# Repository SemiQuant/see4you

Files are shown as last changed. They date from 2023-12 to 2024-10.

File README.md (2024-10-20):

# see4you

A portable OD600 spectrophotometer costing ~$30 (see BOM).
Has a similar dynamic range and comparable reading to the BioRad SmartSpec Plus.

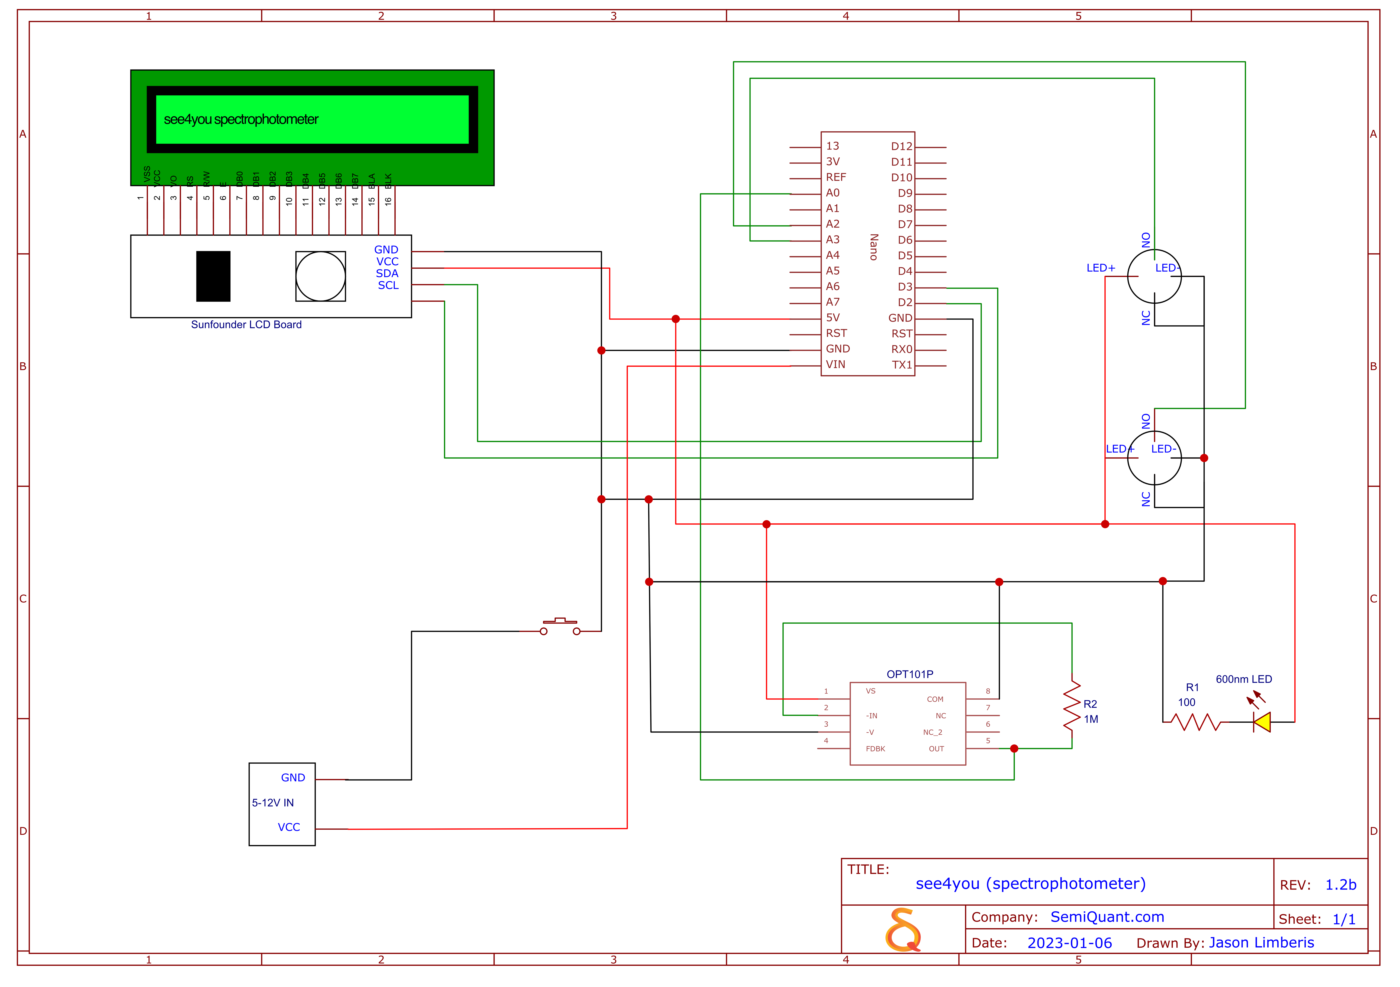
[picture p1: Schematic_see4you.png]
schematic


device

Usage video: 

https://github.com/SemiQuant/see4you/assets/8179171/b92d9823-f1b9-4fbb-b35a-ba92c5bc5852

## version 1b

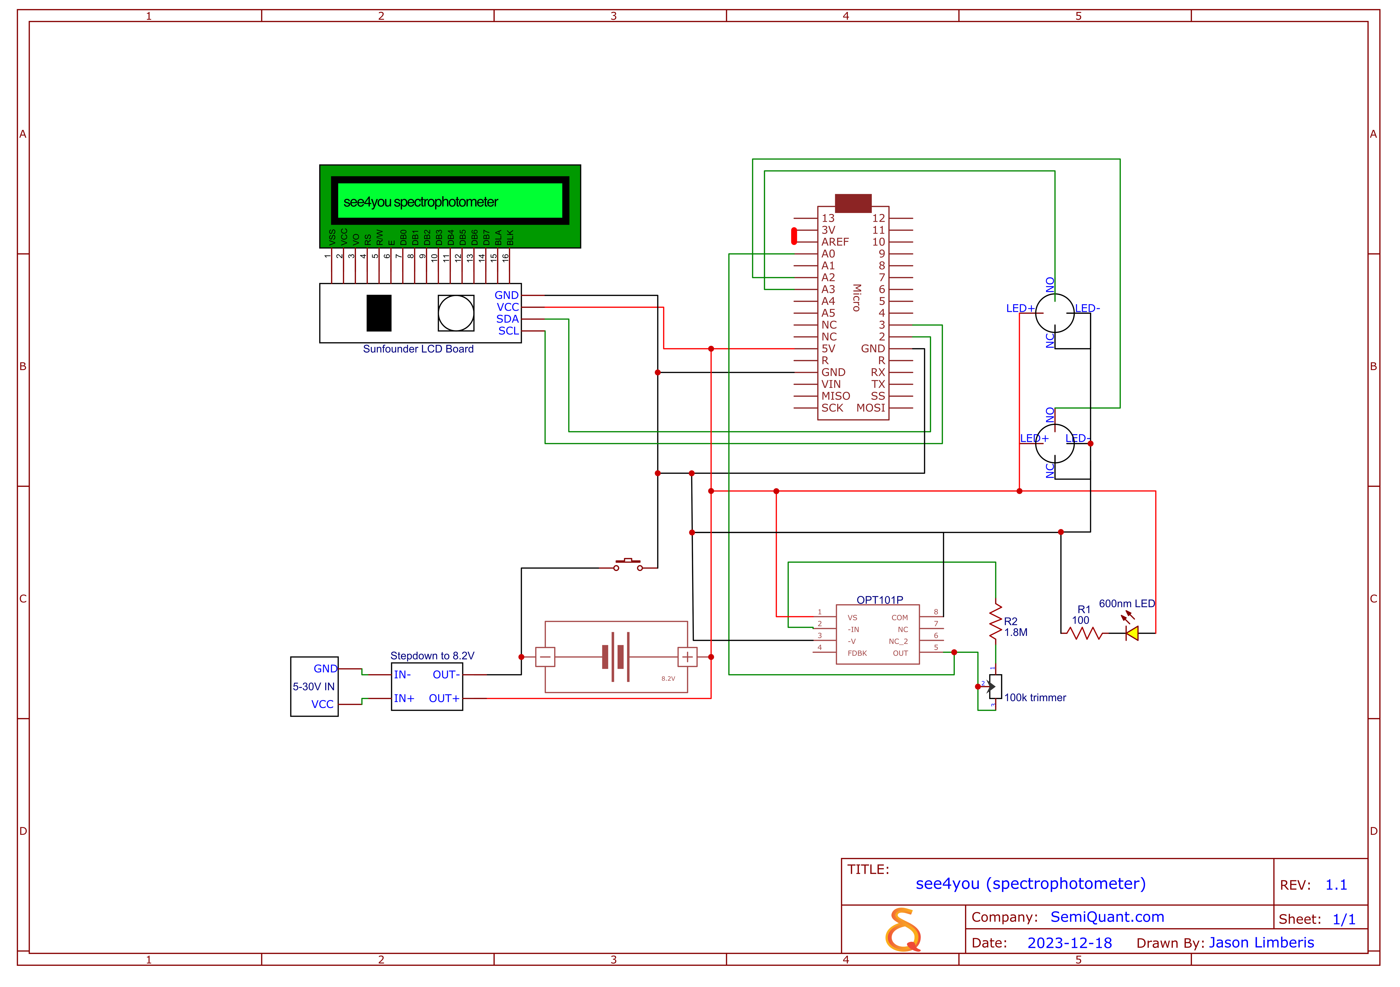
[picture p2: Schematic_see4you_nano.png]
schematic


device

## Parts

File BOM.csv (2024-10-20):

Name | Quantity | Manufacturer Part | Supplier | Price | Link
OPT101 Light light intensity sensor module | 1 | OPT101 | Aliexpress | 2.29 | https://www.aliexpress.us/item/2251832772786039.html
30 AWG Silver Plated Copper | 1 | NA | Aliexpress | 0.99 | https://www.aliexpress.us/item/3256805135541457.html?curPageLogUid=zVtHawfgMBM6
LCD1602 I2C Display Module Blue Green Screen 5V PCF8574 IIC Adapter Llate for Arduino | 1 | LCD 1602 module Blue screen IIC/I2C | Aliexpress | 0.85 | https://www.aliexpress.us/item/3256805913767190.html
Mini / Type-C / Micro USB Nano 3.0 With the bootloader compatible Nano controller for arduino CH340 USB driver 16Mhz ATMEGA328P | 1 | ATMEGA328P | Aliexpress | 1.89 | https://www.aliexpress.us/item/3256805952983310.html?curPageLogUid=sXg4B4DpChgW
Electric Waterproof Power Led Light Momentary Short Mini Push Button Switch | 2 | 3-6v, momentary black | Aliexpress | 1.38 | https://www.aliexpress.us/item/3256801546028835.html
10Pcs KCD1-101 inclined Plane 2Pin Rocker Switch 2 Position | 1 | KCD1-101 inclined plane | Aliexpress | 1.06 | https://www.aliexpress.us/item/3256803951683413.html?curPageLogUid=8yWAwiaaOuQS
100PCS/LOT 1/4W 1R~22M 1% Metal film resistor 100R 220R 1K 1.5K 2.2K 4.7K 10K 22K 47K 100K 100 220 1K5 2K2 4K7 ohm Resistance | 1 | 1.8M ohm resistor | Aliexpress | 0.54 | https://www.aliexpress.us/item/3256802303553096.html?curPageLogUid=oBP9R57Gj4oG
100PCS/LOT 1/4W 1R~22M 1% Metal film resistor 100R 220R 1K 1.5K 2.2K 4.7K 10K 22K 47K 100K 100 220 1K5 2K2 4K7 ohm Resistance | 1 | 100 ohm resistor | Aliexpress | 0.54 | https://www.aliexpress.us/item/3256802303553096.html?curPageLogUid=oBP9R57Gj4oG
50PCS 3mm 5mm DIP Led White Green Blue Yellow Red LED Control Bright On Diode Light No Flicker | 1 | 5mm clear yellow led | Aliexpress | 1.24 | https://www.aliexpress.us/item/3256806140189328.html?curPageLogUid=ZRQjh8IWwZHv
Black Outdoor Waterproof Enclosure Plastic Box Electronic Project Instrument Case Electrical Project Box Junction Box Housing | 1 | 158x90x60 | Aliexpress | 4.01 | https://www.aliexpress.us/item/3256801483869622.html?curPageLogUid=idDUBoIZrthZ
Ultra-Small Size DC-DC Step Down Power Supply Module MP1584EN 3A Adjustable Buck Converter for Arduino Replace LM2596 | 1 | MP1584EN 3A Adjustable Buck Converter | Aliexpress | 0.47 | https://www.aliexpress.us/item/3256803149854639.html?curPageLogUid=joLmRj3Fkpy9
4.8v 3000mah NiMH Battery with Charger cable For Rc toys Cars Tanks Robots Boats Guns Ni-MH AA 4.8 V high capacity Battery Pack | 2 optional | Ni-MH AA 4.8 V | Aliexpress | 5.98 | https://www.aliexpress.us/item/2255800221448318.html
Total | $17
Total with battery | $29

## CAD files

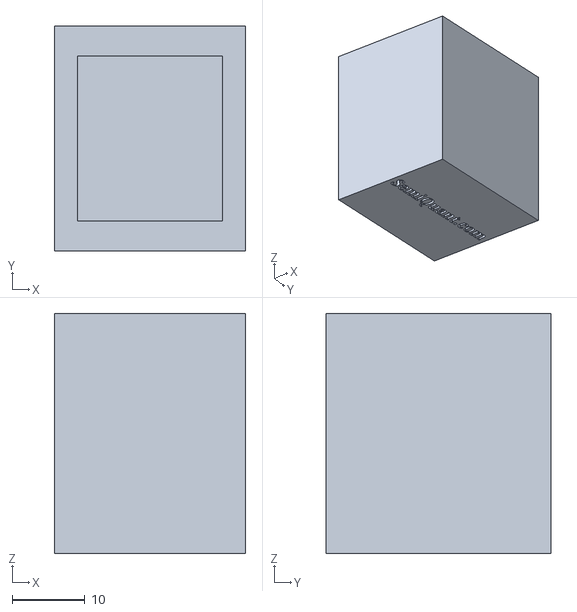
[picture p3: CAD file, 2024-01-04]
cuvette_cover.stl
26.3 x 31.0 x 33.0

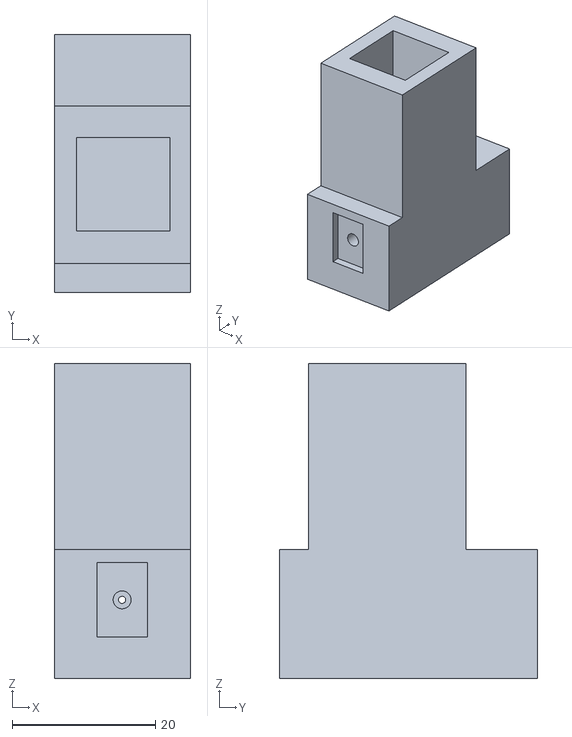
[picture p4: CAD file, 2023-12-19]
cuvette_holder.stl
19.0 x 36.0 x 44.0

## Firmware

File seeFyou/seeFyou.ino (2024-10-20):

#include <Wire.h>
#include <LiquidCrystal_I2C.h>
#include <math.h>

// Arduino pins
// const int output_photodiode = A1;
// const int button_input_blank = A2;
// const int button_input_read = A3;

// ESP32 pins
const int output_photodiode = 27;
const int button_input_blank = 16;
const int button_input_read = 4;

// uncomment this (and below) and connect led to pin 15 if you want it to not stay on continuously, but how else will you know which way to put the cuvette in? lol
// const int ledPin = 15;

float blankReading = 0.0;
float value = 0.0;
LiquidCrystal_I2C lcd(0x27, 16, 2); // set the LCD address to 0x27 for a 16charsand2line display

void setup() {
  Serial.begin(9600);
  Serial.println("Starting");
  //analogReference(EXTERNAL);
  analogReadResolution(10);  
  analogSetWidth(10);              
  analogSetAttenuation(ADC_0db);
  pinMode(output_photodiode, INPUT);
  pinMode(button_input_blank, INPUT_PULLUP);
  pinMode(button_input_read, INPUT_PULLUP);

  // Set welcome screen
  lcd.init(); // initialize the lcd
  lcd.backlight(); // open the backlight
  lcd.setCursor(2, 0); 
  lcd.print("SemiQuant.com"); // Print a message to the LCD
  lcd.setCursor(2, 1); // set the cursor to column 2, line 1
  lcd.print("count4you"); // Print a message to the LCD.

  delay(2000);

  // Show Blank message
  lcd.clear();
  lcd.setCursor(0, 0);
  lcd.print("Blank reading:");
  lcd.setCursor(0, 1);
  lcd.print("Click Blank");
  
  // Wait for button_input_blank to be pressed
  while (digitalRead(button_input_blank) == HIGH) {
    // Wait for the button to be clicked
  }

  lcd.clear();
  lcd.print("Blank reading");
  // Get and display Blank reading
  blankReading = measureIntensity();
  Serial.print(blankReading);
  lcd.clear();
  lcd.setCursor(0, 0);
  lcd.print("Blank reading");
  lcd.setCursor(0, 1);
  lcd.print("Blank read");
  delay(2000);

  // Ask for Read
  lcd.clear();
  lcd.setCursor(0, 0);
  lcd.print("OD reading: ");
  lcd.setCursor(0, 1);
  lcd.print("Click Read");
}

void loop() {
  int buttonState = digitalRead(button_input_blank);
  int buttonState2 = digitalRead(button_input_read);

  // Serial.println(measureIntensity());

  // Serial.println("blankReading1");
  // Serial.println(blankReading);

  // check if the pushbutton is pressed. If it is, the buttonState is HIGH:
  if (buttonState == LOW) {
    lcd.clear();
    lcd.print("Blank reading");
    blankReading = measureIntensity();  // Corrected line
    Serial.print(blankReading);
    lcd.clear();
    lcd.setCursor(0, 0);
    lcd.print("Blank reading");
    lcd.setCursor(0, 1);
    lcd.print("Blank read");
    delay(1000);

    if (blankReading > 850){
      lcd.setCursor(0, 0);
      lcd.print("Underestimates as");
      lcd.setCursor(0, 1);
      lcd.print("blank 0 impedance");
    }
  };

  // Serial.println("blankReading2");
  // Serial.println(blankReading);

  if (buttonState2 == LOW) {
    lcd.clear();
    lcd.print("OD reading:");
    value = measureIntensity();
    
    // Serial.println(value);
    // float od = log10(1.0 / (value / blankReading));
    float od = -log(value / blankReading);

    lcd.setCursor(0, 1);
    if (value > 850 || value < 20 || value >= (blankReading - 4)){
      lcd.print("out of range");
      // lcd.clear();
      // lcd.setCursor(0, 0);
      // lcd.print(blankReading);
      // lcd.setCursor(0, 1);
      // lcd.print(value);
    }else{
      lcd.print(od);
    }
    
    Serial.println("value");
    Serial.println(value);
    Serial.println("blankReading3");
    Serial.println(blankReading);
  };

  delay(500);
}


// this esp is super noisy, can figure out why, so trying to filter that out
// float measureIntensity() {
//     int sumValues = 0;
//     int reads = 0;
//     // digitalWrite(ledPin, HIGH);
//     // delay(500);
//     while (reads < 20) {
//         sumValues += analogRead(output_photodiode);
//         reads++;
//         delay(200);
//     }
//     // digitalWrite(ledPin, LOW);
//     float averageIntensity = sumValues / reads;
//     Serial.println(averageIntensity);  // Print average intensity
//     // averageIntensity = map(averageIntensity, 20, 850, 0, 1000);
//     return averageIntensity;
// }

float measureIntensity() {
    const int maxReads = 10;
    const float tolerance = 0.05; // 5% tolerance
    const unsigned long timeout = 5000; // 5 seconds timeout

    int sumValues = 0;
    int reads = 0;
    float lastIntensity = 0;

    while (true) {
        unsigned long startTime = millis();

        while (reads < maxReads && (millis() - startTime) < timeout) {
            int currentValue = analogRead(output_photodiode);

            if (reads > 0 && abs(currentValue - lastIntensity) / lastIntensity > tolerance) {
                // Skip if the current value differs by more than 5% from the last one
                continue;
            }

             Serial.print(";" + String(currentValue));

            sumValues += currentValue;
            lastIntensity = currentValue;
            reads++;
            delay(200);
        }
        

        if (reads == maxReads) {
            // Successfully obtained 10 consecutive readings within tolerance
            break; // Exit the outer loop
        }

        // Reset variables for a new attempt
        sumValues = 0;
        reads = 0;
    }

    float averageIntensity = sumValues / reads;
    Serial.println(averageIntensity);  // Print average intensity

    return averageIntensity;
}
